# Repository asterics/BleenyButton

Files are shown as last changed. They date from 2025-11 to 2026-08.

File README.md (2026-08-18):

# Bleeny: an nRF52840-based low cost BLE Button

The Bleeny Button is an assistive switch for creating a key press or other HID activities using Bluetooth Low Energy (BLE). It can be used to control SmartPhones, Tablets, Computers or AAC Software like our free and open source [Asterics AAC](https://aac.asterics.eu). The Bleeny Button utilizes the affordable Tenstar Robot devboard (aka nice!nano) or a XIAO nRF52840 board with the Nordic nrf52840 microcontroller. A good summary of the features of this SoC/board is provided at the [Zephyr documentation page](https://docs.zephyrproject.org/latest/boards/others/promicro_nrf52840/doc/index.html). The source code builds with PlatformIO, using the Adafruit nRF52 and Bluefruit libraries. The code is based upon the [BLE keyboard example](https://github.com/adafruit/Adafruit_nRF52_Arduino/blob/master/libraries/Bluefruit52Lib/examples/Peripheral/blehid_keyboard/blehid_keyboard.ino)

## Requirements

* install VSCode/PlatformIO and build a project for the Adafruit Feather nRF52840 Express (or a similar Adafruit nRF board, to install the nRF platform packages) 
* add the files for the nice nano board as described here: [Nicenano-NRF52-Supermini-PlatformIO-Support](https://github.com/ICantMakeThings/Nicenano-NRF52-Supermini-PlatformIO-Support) (not necessary for the XIAO board)

## Usage

* build and upload the demo code (note that the Serial USB CDC interface must be enabled in the code in order to use the auto-upload via DFU in PlatformIO)
* pair the BLE device (e.g. Bleeny-214D, the unique number is composed from the mac address of your device) 
* attach a pushbuttons to GPIO pin 017 and GND (optionally, more buttons can be connected to pins 020, 022, 024 and 100) 
* when pressed, the buttons shall trigger keys (default settings are: `SPACE` , `ENTER`, `1`, `2` and `3`)
* changing settings can be done with the simple config UI (or a serial terminal): __ui/config.html__ or [online](https://assistronik.info/config.html)

### Notes regarding low power operation / current consumption

In paired active mode, current consumption is about 1.2mA @ 3,3V (which can reduced to ~1mA if the activity LED is not used).  
After an adjustable time of user inactivity (constant `SLEEP_TIMEOUT_MS`), the nRF enters hibernation / deep sleep where current consumption drops to 
~1,4uA @ 3,7V. (For this, the LDO for providing external VCC must be disabled, else around 40uA are consumed). This could be further improved by supplying power directly to the VDD pin on the backside of the PCB, see [this post in the Arduino forum](https://forum.arduino.cc/t/nrf52840-development-board-with-adafruit-nrf52-core/1290505/6)
A wakeup can be triggered by pressing any of the configured buttons. This will cause a system reset. BLE connection to a paired host is usually re-established in 1-3 seconds. 

## Suggested hardware setup

### 3D printed parts

You need to print following files from the `hw` folder:

* _0-1-ProMicro_Basic.stl_ (Tenstar Board, one button) __OR__ _0-2-ProMicro_Output.stl_ (Tenstar Board, button + output jack plug with a relay __OR__ _0-3-XIAO_Basic.stl_ (XIAO nRF52840 Board, one button) __OR__ _0-3-XIAO_Output.stl_ + _0-3-XIAO_Output_Clip.stl_ (XIAO nRF52840 board, button + output jack plug with a relay)
* _1-Ring.stl_
* _2-Topper.stl_

### Electronic / mechanical parts

* Tenstar nRF52840 Pro Micro (nice!nano) __OR__ [XIAO nRF52840](https://www.tme.eu/at/en/details/seeed-102010448/development-kits-for-data-transmission/seeed-studio/xiao-nrf52840/)
* [Tactile push button 12x12mm, 8.5mm height](https://www.tme.eu/at/en/details/tl3300cf160q/microswitches-tact/e-switch/)
* [170mA LiPo battery](https://www.pollin.de/p/lithium-polymer-akku-hwe601525-3-7-v-170-mah-5-stueck-273699)
* [3x M2x8mm screw](https://www.tme.eu/at/en/details/m2x8_d7985-a2/bolts/kraftberg/)

Optional (if using the BleenyButton with the output enabled):

* [FTR-B3GB003Z](https://www.tme.eu/at/en/details/ftr-b3gb003z/miniature-electromagnetic-relays/fcl-components/) mini relay, latching, 3V
* [FC68125](https://www.tme.eu/at/en/details/fc68125/jack-connectors/cliff/) 3.5mm jack
* 6x6mm Button, 8.35mm length (mode switching)

### Assembly

Please have a look at the pictures named __wiring_*__ in the folder `img`, select the correct picture for your setup (Tenstar or XIAO board, button only or with output)

1. Glue the parts into the case, either use hotglue or mounting adhesive (recommended!)

   Note 1: avoid glue in the USB-C connector and the jack plug (if mounted)

   Note 2: do not glue any contacts, soldering will result in hazardous fumes

2. Solder the button and optional relay/jackplug

   Note: avoid short circuits if using bare wire

   Note: also solder the shown bridges if using relay/jackplug

3. Solder the battery

   Note: avoid any short circuits with the battery! Especially when removing the plug or the insulation.

   Note: on the XIAO board, the LEDs will blink if the battery is connected correctly

4. Place the topper on the base, add the ring. Hold the ring & base and screw them together (M2x8 screws, 3x)

### Programming

* Open this folder with VSCodium (or VSCode if prefer M$ tracking)
* Select the correct target in PlatformIO:
  * XIAO nRF52840: `[env:xiao_nrf52840]`
  * Tenstar: Follow the [installation guide](https://github.com/ICantMakeThings/Nicenano-NRF52-Supermini-PlatformIO-Support) , build an example and the build with `[env:nicenano]`
* With relay/jackplug: enable `//#define OUTPUT_ACTIVE`
* Upload

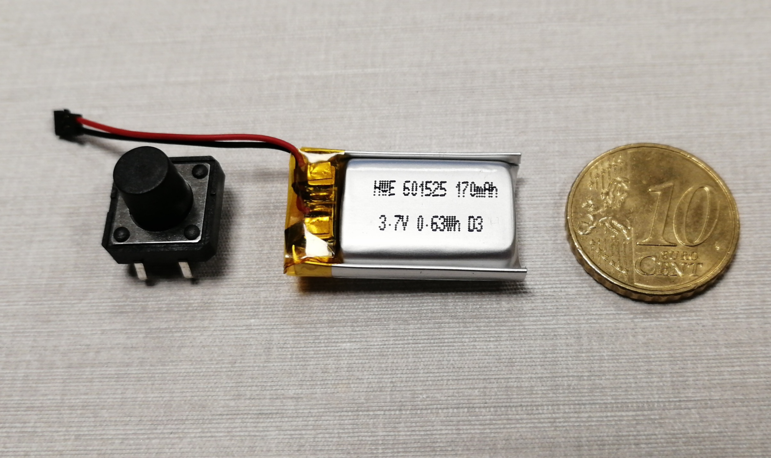
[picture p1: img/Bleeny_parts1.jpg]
parts and size comparison

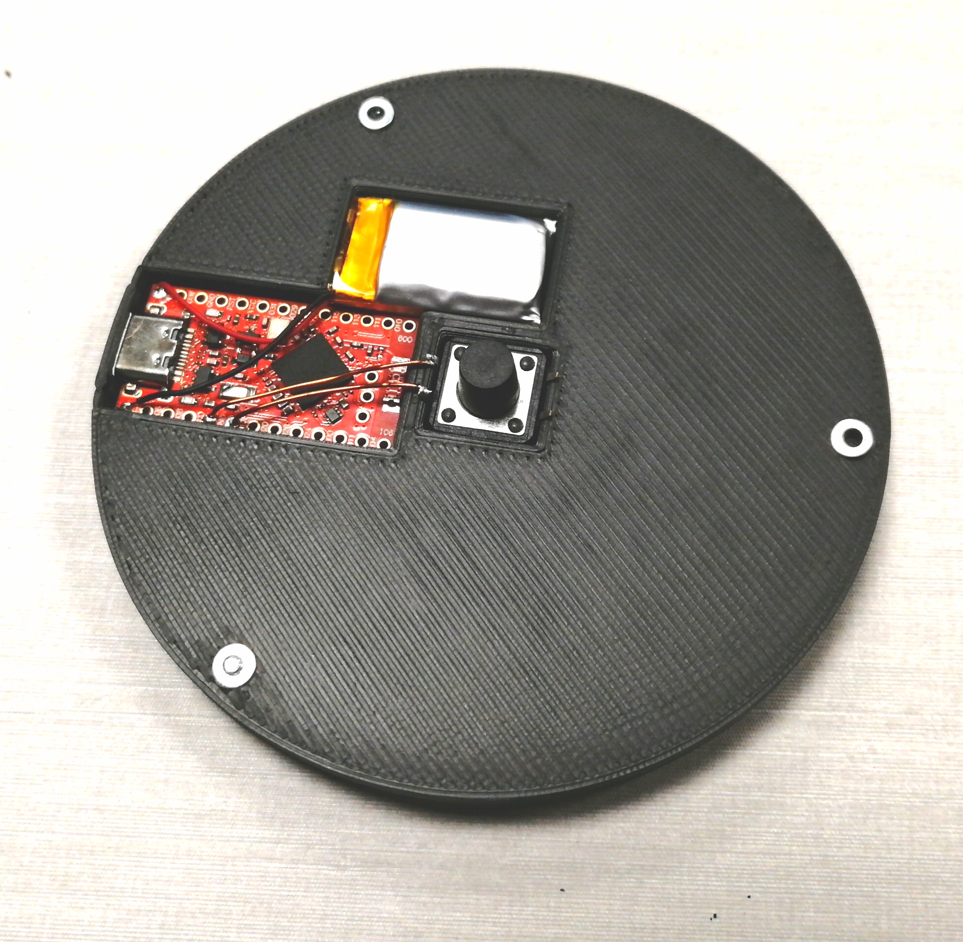
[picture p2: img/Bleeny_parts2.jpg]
parts mounted in base

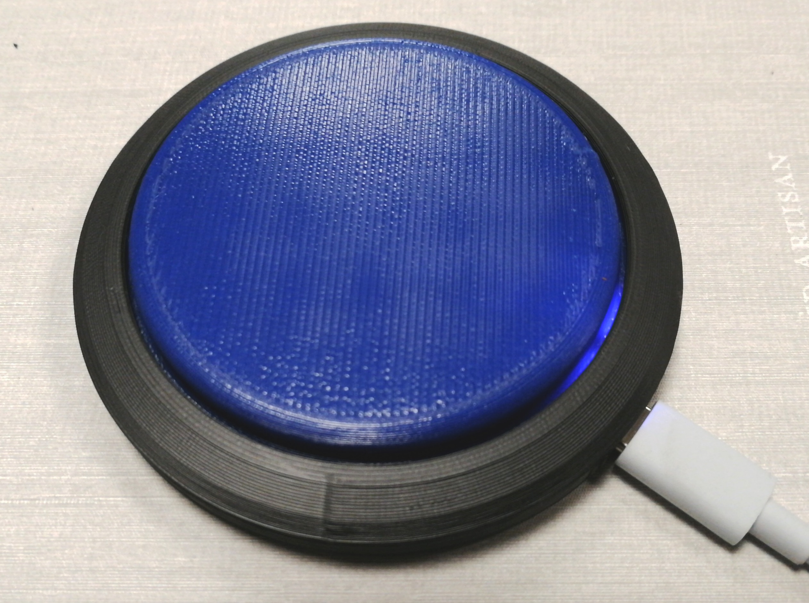
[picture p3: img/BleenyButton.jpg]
assembled Bleeny Button


## Configuration (UI)

The BleenyButton can be configured via the USB-CDC (USB-Serial) interface. An unknown/empty command or `?\n` prints out the help with possible commands. This is used for UI as well, which shows the possible options based on the help output.

Open the UI either by opening the file `/ui/config.html` with a browser (not in GitHub!) locally OR open it at [https://assistronik.info/config.html](https://assistronik.info/config.html).

Press __connect__ and select the BleenyButton serial interface (shown as something with nRF52840).

The UI will show you the possible options.

### Key combination assignment

Key 1 and Key 2 support any key or key combination (e.g. `Alt+H`, `Ctrl+Shift+Z`, `F13`). In the web UI, click the **Key 1** or **Key 2** field and press the desired key (with any modifiers held down) — the field auto-detects and displays the combination. Click **Update** to send it to the device, then **Store new settings** to save.

The serial command format is `1:<keycode>:<modifier>` where both values are decimal USB HID codes (e.g. `1:11:4` sets Key 1 to `Alt+H`). Modifier bits: Ctrl=0x01, Shift=0x02, Alt=0x04, GUI/Win=0x08.

> **Note:** Some browser/OS shortcuts (e.g. `Ctrl+W`, `Alt+F4`) are intercepted before reaching the web UI. Use the serial terminal for those combinations.

__Important:__ The settings are not saved automatically, you need to execute __Store new settings on the device__!

### Currently implemented settings

| Command                                     | Shortcode (serial command) | Type & Value Range                                   | Notes                                                        |
| ------------------------------------------- | -------------------------- | ---------------------------------------------------- | ------------------------------------------------------------ |
| Store new settings on the device            | s                          | Action                                               | Always trigger this action to save changes                   |
| Inactivity time [ms]                        | i                          | Integer, 30000-600000 [ms] (30s - 10min)             | Time before the BleenyButton enters the power-down mode. Will be reset by pressing the button or an established BLE connection |
| Connected device                            | d                          | Info                                                 | This information heavily depends on the BLE stack of the host device, it is not always available, even if a device is connected! |
| Reset paired devices                        | r                          | Action                                               | Reset the BLE pairings                                       |
| Key 1                                       | 1                          | Key combination (any key + optional modifiers Ctrl/Shift/Alt/GUI) | Select the keyboard key or key combination to send when pressing the main button. Use the web UI to auto-detect by pressing the desired key. |
| Key 2                                       | 2                          | Key combination (any key + optional modifiers Ctrl/Shift/Alt/GUI) | If a second button is connected, this key combination will be sent. |
| Print out supported commands and build date | ?                          | Action                                               | Print out possible commands                                  |

The following commands are available when building with output enabled:

| Command                   | Shortcode (serial command) | Type & Value Range              | Notes                                                        |
| ------------------------- | -------------------------- | ------------------------------- | ------------------------------------------------------------ |
| Trigger output            | c                          | Action                          | Trigger the output, either click or toggle (see Output mode) |
| Output mode               | o                          | Selection: click, toggle        | Either click the output for 0.1s or toggle when the button is pressed (or command "Trigger output" is sent) |
| Mode 1 - Tremor timeout   | t                          | Integer, 300-5000 [ms] (0.3-5s) | Defines the delay before another output trigger can happen, used in Mode 1 |
| Mode 3 - Auto click delay | p                          | Integer, 2-600 [s]              | After the output is triggered, this time will pass until the output is triggered again. |
| Startup Mode              | m                          | Integer, 1-4                    | Select the output mode on startup. The mode can be changed with the second button on the bottom (PIN_MODE) |

### Output mode description

#### Mode 1 - tremor timeout

When pressing the button, it is locked for a given timeout until another press on the button is triggering the output.

#### Mode 2 - straight

Button presses are directly mapped to the output. Note: each edge (press / release) triggers the output (either click or toggle).

#### Mode 3 - auto click

A button press triggers the output. Afterwards, the button is locked for a given timeout, then another automatic trigger of the output happens.

#### Mode 4 - disabled

The relay output is fully disabled. Button presses only send the configured BLE key — no relay switching occurs.

 # Acknowledgement

This work has been accomplished at the UAS Technikum Wien in course of the R&D-project [InDiKo](https://www.technikum-wien.at/en/research-projects/indiko/) (MA23 project 38-09), which is supported by the [City of Vienna](https://www.wien.gv.at/kontakte/ma23/index.html).

FreeCAD project, output addition, XIAO board adaption and software bugfixes are done by Benjamin Aigner, [Assistronik](https://assistronik.info)

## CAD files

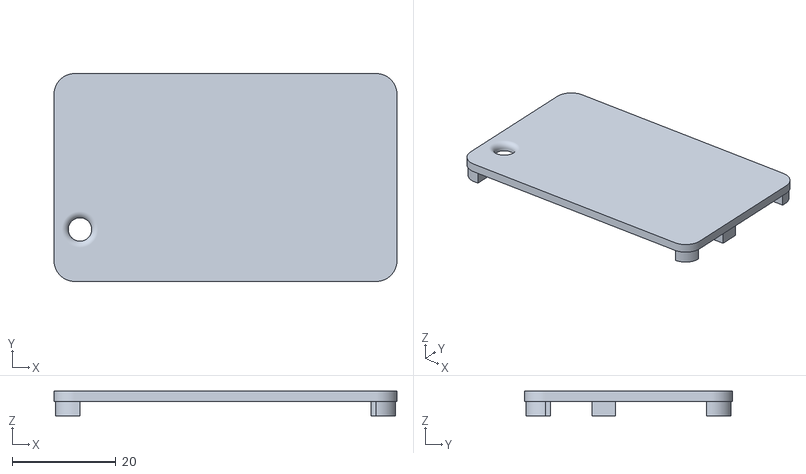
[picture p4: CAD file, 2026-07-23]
hw/BleenyRCV_lid.stl
66.0 x 40.0 x 4.75

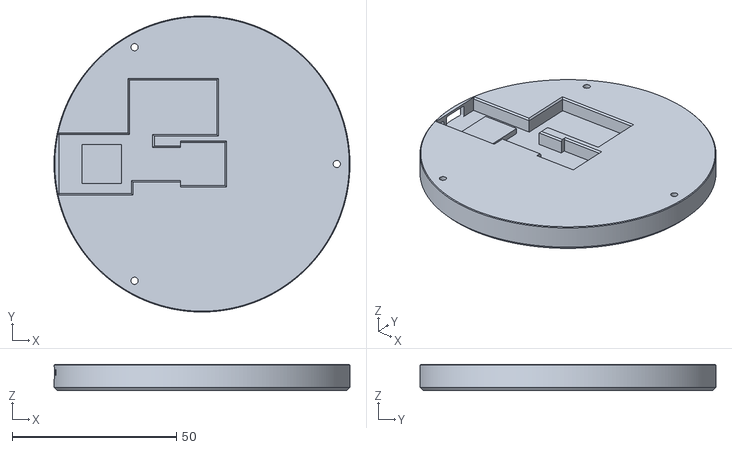
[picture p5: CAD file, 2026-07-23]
hw/0-3-XIAO_Basic.stl
90.0 x 90.0 x 8.00

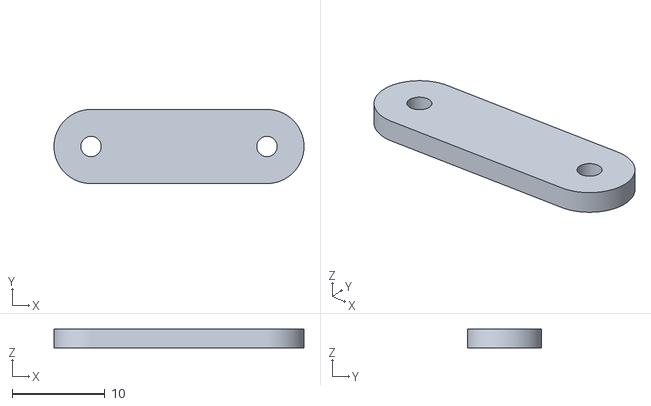
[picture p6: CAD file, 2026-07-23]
hw/0-3-XIAO_Output_Clip.stl
27.0 x 8.00 x 2.00

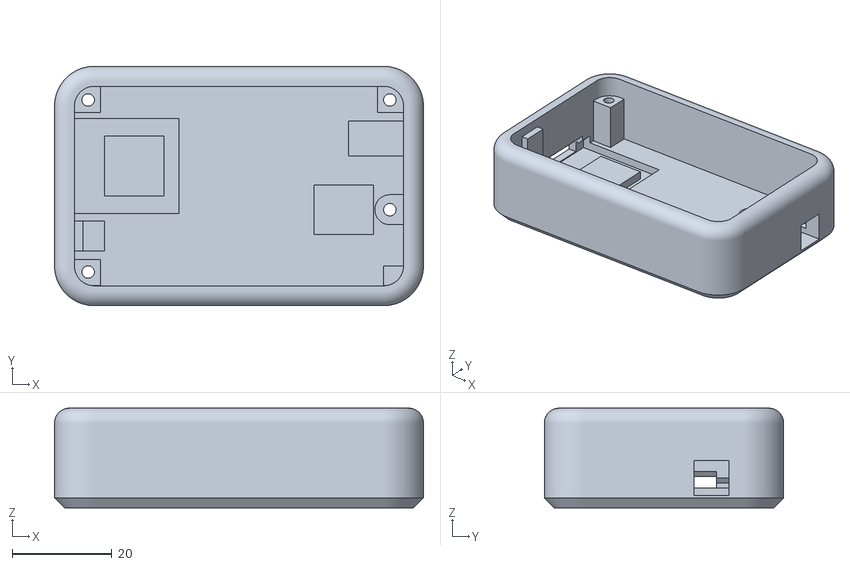
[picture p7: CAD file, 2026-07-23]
hw/BleenyRCV_base.stl
74.0 x 48.0 x 20.0

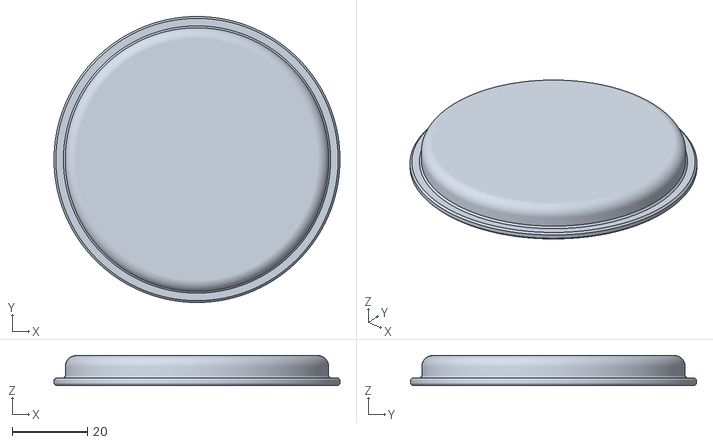
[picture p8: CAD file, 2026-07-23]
hw/2-Topper.stl
76.0 x 76.0 x 8.00

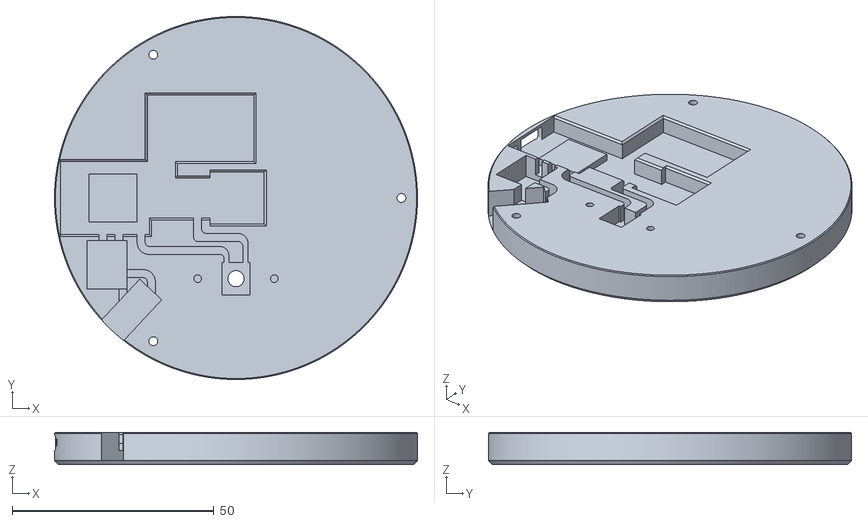
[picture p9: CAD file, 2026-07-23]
hw/0-3-XIAO_Output.stl
90.0 x 90.0 x 8.00

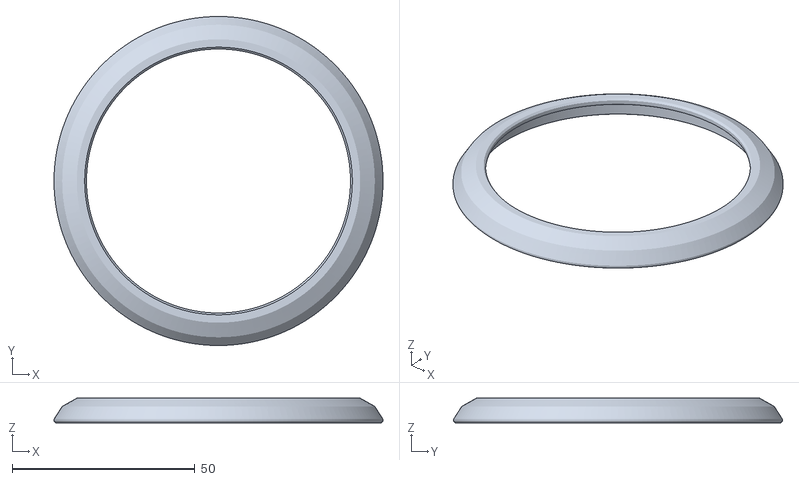
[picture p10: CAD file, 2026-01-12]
hw/1-Ring.stl
90.0 x 90.0 x 6.75

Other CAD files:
hw/0-1-ProMicro_Basic.stl
hw/Bleeny_case.FCStd
hw/0-2-ProMicro_Output.stl

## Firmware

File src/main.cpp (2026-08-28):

// Tenstar nrf52840 (aka nice!nano) BLE keyboard button demo
//
// this demo is based upon:
// https://github.com/ICantMakeThings/Nicenano-NRF52-Supermini-PlatformIO-Support
//
// Adafruit nrf52 Arduino library and BLE keyboard example:
// https://github.com/adafruit/Adafruit_nRF52_Arduino/blob/master/libraries/Bluefruit52Lib/examples/Peripheral/blehid_keyboard/blehid_keyboard.ino
//
// see also:
// https://forum.arduino.cc/t/nrf52840-development-board-with-adafruit-nrf52-core/1290505/6


#include <Arduino.h>
#include <bluefruit.h>
#include "Adafruit_LittleFS.h"
#include "gpio_helper.h"
#include "InternalFileSystem.h"

#define EXT_LOW_PIN 13

#define ENABLE_ACTIVITY_LED 1
#define ENABLE_DEBUG_OUTPUT 1  // set to 1 to enable serial debug output; 
#define STARTUP_WAIT_SERIAL 0  // wait for Serial to be connected on startup. Note: this applies after wakeups too!

// sleep configuration
uint sleep_timeout_ms = 180000;  // Sleep after 180 seconds of inactivity
unsigned long lastActivityTime = 0;
bool sleepMode = false;

// define ASCII-key action for each button
#define NUM_BUTTONS 4
uint8_t button_map[NUM_BUTTONS] = {BUTTON1, BUTTON2, BUTTON3, BUTTON4};
// HID keycode for each button (USB HID Usage Tables: A=0x04, Space=0x2C, Enter=0x28, ...)
uint8_t button_keycodes[NUM_BUTTONS] = {HID_KEY_SPACE, HID_KEY_ENTER, HID_KEY_1, HID_KEY_2};
// HID modifier byte per button (Ctrl=0x01, Shift=0x02, Alt=0x04, GUI=0x08; OR for combinations)
uint8_t button_modifiers[NUM_BUTTONS] = {0, 0, 0, 0};
// Action type per button: 0=key press, 1=left click, 2=right click, 3=scroll up, 4=scroll down
uint8_t button_actions[NUM_BUTTONS] = {0, 0, 0, 0};
uint8_t buttonStates = 0;

// Multi-key state (up to 6 simultaneous keys)
static uint8_t active_keys[6] = {0};

BLEDis bledis;
BLEHidAdafruit blehid;
//settings handling and parser at the end of the file
void loadSettings();
bool storeSettings();
using namespace Adafruit_LittleFS_Namespace;
File file(InternalFS);
void parseCommand(char *buf);
void printHelp();
#define MAX_PARAM_LEN 32

/******* output to 3.5mm jackplug ******/
//use output functions ('c' command)
//#define OUTPUT_ACTIVE

#ifdef OUTPUT_ACTIVE
  //latching 1 coil relay on P0.02 (D18) & P0.29 (D20)
  uint8_t pin_out[2] = {OUT1,OUT2};
  //different modes for the output
  int mode = 0; 
  // how many modes are used
  #define MODE_MAX 4
  //pin for the mode switch button
  uint8_t pin_mode = PIN_MODE; 
  //output mode: 0: click the output on each action; 1: toggle the output on each action
  int output_mode = 0;
  //f-prototypes to control the output
  uint tremor_timeout_ms = 1000;
  uint pause_timeout_s = 5;
  void triggerOutput();
  void output(bool on);
  void handleOutput(bool pressed, bool released);
#endif

void enterSleepMode() {
  //if charge state pin is enabled, check: when charging don't enter sleep mode
  #ifdef CHARGE_STATE
    if(dRead(CHARGE_STATE) == LOW) {
      if(ENABLE_DEBUG_OUTPUT) Serial.println("Charging, don't enter sleep mode");
      lastActivityTime = millis();
      return;
    }
  #endif
  //if we have the battery state on a voltage divider, disable it when entering sleep mode
  //note: don't set this to input when charging, worst case: 4.2V on GPIO pin...
  #ifdef VBATT_DIVIDER_LOW
    dMode(VBATT_DIVIDER_LOW,INPUT);
  #endif

  if (ENABLE_DEBUG_OUTPUT) { Serial.println("Entering sleep mode..."); delay(50); } /*delay in debug is necessary to still print out via USB.*/
  sleepMode = true;
  
  // Configure all button pins as wakeup sources with pullup
  uint32_t ulPin;

  for (uint8_t i = 0; i < NUM_BUTTONS; i++) {
    //ignore unused pins
    if(button_map[i] > NUMBER_OF_PINS) continue;

    //map pins to correct port & pin
    ulPin = button_map[i];
    NRF_GPIO_Type * port = nrf_gpio_pin_port_decode(&ulPin);

    // Set pin as wake source (low level trigger)
    port->PIN_CNF[ulPin] = (GPIO_PIN_CNF_SENSE_Low << GPIO_PIN_CNF_SENSE_Pos) |
                                       (GPIO_PIN_CNF_DRIVE_S0S1 << GPIO_PIN_CNF_DRIVE_Pos) |
                                       (GPIO_PIN_CNF_PULL_Pullup << GPIO_PIN_CNF_PULL_Pos) |
                                       (GPIO_PIN_CNF_INPUT_Connect << GPIO_PIN_CNF_INPUT_Pos) |
                                       (GPIO_PIN_CNF_DIR_Input << GPIO_PIN_CNF_DIR_Pos);
  }
  
  // Turn off LED to save power
  if (ENABLE_ACTIVITY_LED) dWrite(LED_R, !LED_ON);
  #ifdef LED_G 
    dWrite(LED_G,!LED_ON); 
  #endif
  #ifdef LED_B
    dWrite(LED_B,!LED_ON);
  #endif

  //TODO: if on XIAO: disable res-divider for batt voltage
  
  // Put nRF52 into low power mode
  sd_power_system_off();
  // This line won't be reached as system_off() causes a reset
}

bool addActiveKey(uint8_t keycode) {
  if (!keycode) return false;
  for (uint8_t i=0;i<6;i++) if (active_keys[i] == keycode) return false; // already
  for (uint8_t i=0;i<6;i++) if (active_keys[i] == 0) { active_keys[i] = keycode; return true; }
  return false; // full
}

bool removeActiveKey(uint8_t keycode) {
  bool removed = false;
  for (uint8_t i=0;i<6;i++) if (active_keys[i] == keycode) { active_keys[i] = 0; removed = true; }
  return removed;
}

void startAdv(void)
{  
  // Advertising packet
  Bluefruit.Advertising.addFlags(BLE_GAP_ADV_FLAGS_LE_ONLY_GENERAL_DISC_MODE);
  Bluefruit.Advertising.addTxPower();
  Bluefruit.Advertising.addAppearance(BLE_APPEARANCE_HID_KEYBOARD);

  // Include BLE HID service
  Bluefruit.Advertising.addService(blehid);

  // There is enough room for the dev name in the advertising packet
  Bluefruit.Advertising.addName();
  
  /* Start Advertising
   * - Enable auto advertising if disconnected
   * - Interval:  fast mode = 20 ms, slow mode = 152.5 ms
   * - Timeout for fast mode is 30 seconds
   * - Start(timeout) with timeout = 0 will advertise forever (until connected)
   * 
   * For recommended advertising interval
   * https://developer.apple.com/library/content/qa/qa1931/_index.html   
   */
  Bluefruit.Advertising.restartOnDisconnect(true);
  Bluefruit.Advertising.setInterval(32, 244);    // in unit of 0.625 ms
  Bluefruit.Advertising.setFastTimeout(30);      // number of seconds in fast mode
  if (!Bluefruit.Advertising.start(0)) {          // 0 = Don't stop advertising after n seconds
    if (ENABLE_DEBUG_OUTPUT) Serial.println("ERROR: Failed to start advertising!");
  } else {
    if (ENABLE_DEBUG_OUTPUT) {
      char name_buffer[64];
      if (Bluefruit.getName(name_buffer, sizeof(name_buffer)) > 0) {
        Serial.print("Advertising as: ");
        Serial.println(name_buffer);
      }    
    }
  }
}


void setup() 
{
  //if on XIAO: enable res-divider (might be dangerous: charging & disabled res-divider...)
  //https://wiki.seeedstudio.com/XIAO_BLE/#q3-what-are-the-considerations-when-using-xiao-nrf52840-sense-for-battery-charging
  #ifdef VBATT_DIVIDER_LOW
    dMode(VBATT_DIVIDER_LOW,OUTPUT);
    dWrite(VBATT_DIVIDER_LOW,LOW);
  #endif
  #ifdef CHARGE_STATE
    dMode(CHARGE_STATE,INPUT_PULLUP);
  #endif

  if (ENABLE_DEBUG_OUTPUT) {
    Serial.begin(115200);  // note: the USB CDC serial port is not only useful for debugging
                         // but also for resetting the nRF52 when uploading code via the bootloader
    if(STARTUP_WAIT_SERIAL) {
      while ( !Serial ) delay(10);   // wait until Serial is connected 
    }
    Serial.println("BleenyButton by AsTeRICS Foundation / Assistronik ready");
  }

  for ( uint8_t i=0; i<NUM_BUTTONS; i++ ) {
    dMode( button_map[i], INPUT_PULLUP );
  }

  if (ENABLE_ACTIVITY_LED) {
    dMode(LED_R, OUTPUT);  //Set the LED to output mode.
  }

  dMode(EXT_LOW_PIN, OUTPUT); 
  //OUTPUT_H0H1 //high drive sink & source
  dWrite(EXT_LOW_PIN, LOW); // turn off external LDO to save power

  //if output is active, activate GPIOs in high drive mode
  #ifdef OUTPUT_ACTIVE
  dMode(pin_out[0], OUTPUT_H0H1);
  dMode(pin_out[1], OUTPUT_H0H1);
  dMode(pin_mode, INPUT_PULLUP);
  #endif

  loadSettings();

 
  if (!Bluefruit.begin()) {
    if (ENABLE_DEBUG_OUTPUT) Serial.println("ERROR: Failed to initialize Bluefruit!");
    while(1);
  }

  Bluefruit.setTxPower(4);    

  // Get MAC address and create unique advertising name
  uint8_t mac[6];
  Bluefruit.getAddr(mac);
  char name_buffer[64]={0};
  sprintf (name_buffer, "Bleeny-%02X%02X", mac[4], mac[5]);
  Bluefruit.setName(name_buffer);
  //not used, we read out the connected device in printHelp()
  //Bluefruit.Periph.setConnectCallback(connect_callback);

  // Configure and Start Device Information Service
  bledis.setManufacturer("AsTeRICS Foundation / Assistronik");
  bledis.setModel("BleenyButton");
  bledis.begin();

  /* Start BLE HID
   * Note: Apple requires BLE device must have min connection interval >= 20m
   * ( The smaller the connection interval the faster we could send data).
   * However for HID and MIDI device, Apple could accept min connection interval 
   * up to 11.25 ms. Therefore BLEHidAdafruit::begin() will try to set the min and max
   * connection interval to 11.25  ms and 15 ms respectively for best performance.
   */
  blehid.begin();

  /* Set connection interval (min, max) to your perferred value.
   * Note: It is already set by BLEHidAdafruit::begin() to 11.25ms - 15ms
   * min = 9*1.25=11.25 ms, max = 12*1.25= 15 ms 
   */
  /* Bluefruit.Periph.setConnInterval(9, 12); */

  // Set up and start advertising
  startAdv();

  lastActivityTime = millis();  // initialize activity timer
}
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

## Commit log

2025-11-08 updated Readme, added data about current consumption
2025-11-10 improve current consumption in sleep mode (turned off external LDO)
2025-11-14 added stl files for 3d-printed enclosure
    [BleenyButton-Base.stl, BleenyButton-Ring.stl, BleenyButton-Topper.stl]
2026-01-12 Added FreeCAD based case
    [Bleeny_case-Base.stl, Bleeny_case-Ring.stl, Bleeny_case-Topper.stl, Bleeny_case.FCStd]
2026-01-12 screw holes in ring were too big
    [Bleeny_case-Ring.stl, Bleeny_case.FCStd]
2026-01-14 Added UI & config storing and other changes:
    - reduced GPIO map to 4; bank 1 might be problematic with wakeup & register writing
    - split up GPIO pin map into "reading" and "wakeup"
    - GPIO pinning is messed up with nRF52, no standardized pin names and digitalWrite always looks up pin numbers to real pin numbers
    - added load & store settings in LittleFS (nearly no overhead, LittleFS/InternalFS is already used for BLE pairings)
    - added commands to change settings (single char cmd), possible commands via help ('?')
    - added webui which dynamically gets settings via '?' and allows basic configuration
2026-01-15 Added current value in the UI
2026-01-15 Updated case and added base with jack plug and button
    [Bleeny_case-Base.stl, Bleeny_case-Base_JackOut.stl, Bleeny_case-Topper.stl, Bleeny_case.FCStd]
2026-01-29 added transport clips for preventing button press in box
    [Bleeny_case-transport_clip_1.stl, Bleeny_case-transport_clip_2.stl, Bleeny_case.FCStd]
2026-01-29 Renamed .stl files; select option for 0 (ProMicro/XIAO and Basic/with Output)
    [0-1-ProMicro_Basic.stl, 0-2-ProMicro_Output.stl, 0-3-XIAO_Basic.stl, 0-3-XIAO_Output.stl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]
2026-01-30 major changes:
    - added commands to change the keycode for buttons
    - UI improvements (enum handling; added info as type)
    - added XIAO target in PIO
    - changed all the sh***ty arduino pin names into nRF port+pin
    - removed the ASCII handling, working with keycodes (won't be support something like keyboard.print)
2026-01-30 Added some graphics how to wire things up
2026-01-30 Added wiring for XIAO; fixed STL for XIAO Output (Tip wasn't set correctly)
    [0-3-XIAO_Output.stl, Bleeny_case.FCStd]
2026-02-02 Added vbatt pin handling (must not be floating when charging!)
2026-02-02 added a small clip for the mode button.
    [0-3-XIAO_Output.stl, 0-3-XIAO_Output_Clip.stl, Bleeny_case.FCStd]
2026-03-16 Actuator of topper lower -> for buttons of official distributors
    [2-Topper.stl, Bleeny_case.FCStd]
